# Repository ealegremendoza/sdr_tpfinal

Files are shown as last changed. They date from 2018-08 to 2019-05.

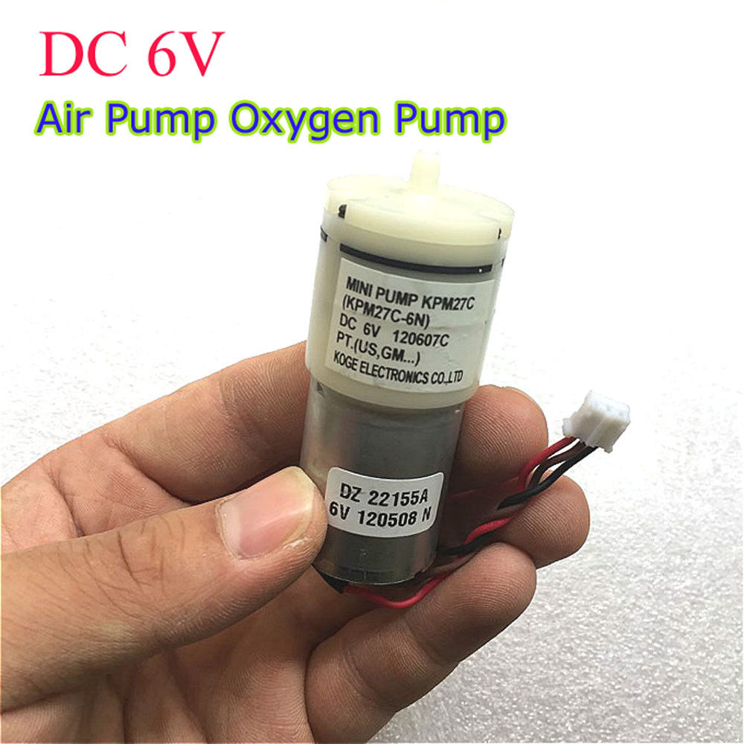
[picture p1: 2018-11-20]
docs/air_pump_1.jpg

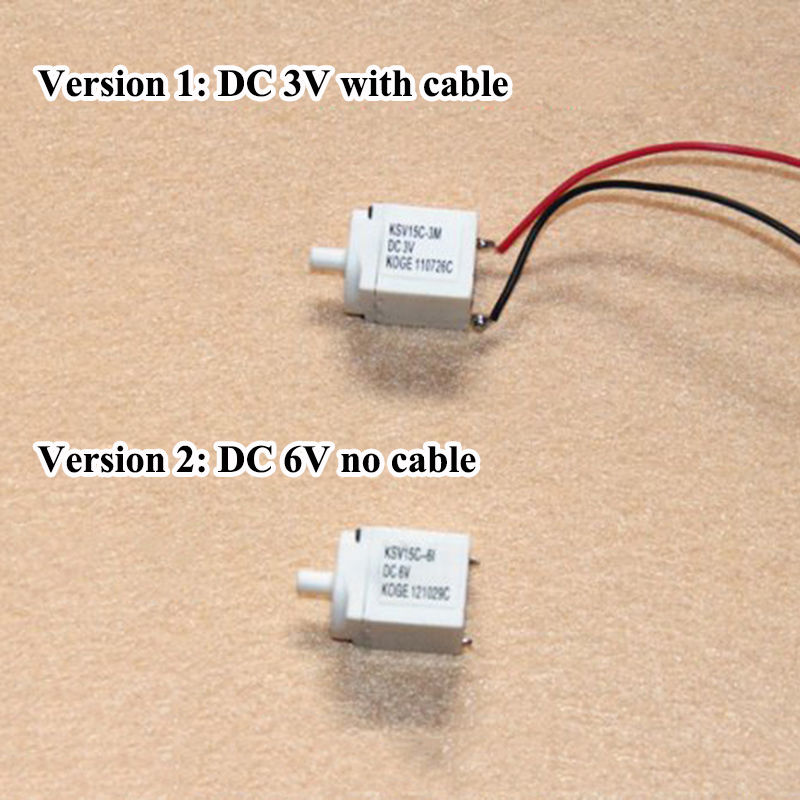
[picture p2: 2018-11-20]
docs/valve6.jpg

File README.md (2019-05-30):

# Proyecto Final de SDR 
## TENSIOMETRO DIGITAL

> TP Final de la materia Sistemas de Representación R1032 UTN FRBA. Ciclo lectivo 2018.

## Carpetas
>- *docs*: es encuentran archivos de interés para el proyecto.
>- *pcb*: desarrollo de la placa del proyecto.

---

Espero le sea de utilidad.

Ezequiel Alegre 

>Toda sugerencia será bienvenida.

>ealegremendoza@gmail.com

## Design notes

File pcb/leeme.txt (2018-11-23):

Guía de directorios y archivos más importantes:

/TensiometroDigital					-Contiene todo el trabajo práctico.
	
	PCB Layout Checklist.xslx			-Checklist

	/BOM						-Contiene la BOM del trabajo práctico. 
		TensiometroDigital_BOM_LINK_OCTOPART	-Contiene el link a la BOM en octopart.com
	
	/GABINETE
		GABINETE.fcstd1				-Contiene el gabinete creado en FREECAD.

	/GERBERS					-Contiene los archivos gerbers del PCB.

	/INFORME
		TensiometroDigita_informe.pdf		-Informe del trabajo práctico.

	/PANEL						-Contiene el panelizado del PCB.
		/panel-gerbers				-Contiene los archivos gerbers del panel.

	/PDFs
		TensiometroDigital-SCH_v1.pdf		-Esquemáticos del trabajo práctico.
		TensiometroDIgital-PCB_v1.pdf		-PCB del trabajo práctico.
		TD-gabinete-base-drawings_v1.pdf	-Drawings de la BASE del gabinete del trabajo práctico.
		TD-gabinete-tapa-drawings_v1.pdf	-Drawings de la TAPA del gabinete del trabajo práctico.

- El resto de los directorios y archivos no mencionados aquí son auxiliares para realizar el trabajo práctico.

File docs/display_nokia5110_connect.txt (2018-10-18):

https://www.algissalys.com/how-to/nokia-5110-lcd-on-raspberry-pi

Raspberry PI (physical pins)		5110 LCD

18	GPIO 24				RST (RESET)
24	SPI_CE0				CE (CHIP ENEABLE)
16 	GPIO 23				DC (DATA)
19	SPI_MOSI			DIN
23	SPI_SCLK			CLK
1	VCC 3.3V			VCC
11	GPIO 17				LIGHT
6	GND				GND

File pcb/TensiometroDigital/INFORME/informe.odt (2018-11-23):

# Descripción del proyecto diseñado

El siguiente proyecto es un medidor de presión arterial digital que utiliza un sensor de presión integrado, circuitos de acondicionamiento de señal analógica, un microcontrolador, una pantalla de cristal líquido y una memoria SD para el almacenamiento de datos.

El sistema de detección lee la presión del manguito (CP) y extrae los pulsos para el análisis y la determinación de la presión sistólica y diastólica. Este diseño utiliza un sensor de presión integrado de 50 kPa (Freescale Semiconductor, Inc. P / N: MPXV5050GP) que produce un rango de presión de 0 mm Hg a 300 mm Hg.

## Concepto del método oscilométrico

Este método es empleado por la mayoría de los dispositivos no invasivos automatizados. Una extremidad y su vasculatura están comprimidas por un manguito de compresión inflable y envolvente. La lectura de la presión arterial para los valores de presión arterial sistólica y diastólica se lee en el punto de identificación del parámetro.
El principio de medición simplificado del método oscilométrico es una medición de la amplitud del cambio de presión en el brazalete cuando el manguito se infla por encima de la presión sistólica. La amplitud aumenta repentinamente a medida que el pulso se rompe a través de la oclusión. Esto está muy cerca de la presión sistólica. A medida que la presión del manguito se reduce aún más, la pulsación aumenta en amplitud, alcanza un máximo y luego disminuye rápidamente. El índice de presión diastólica se toma donde comienza esta rápida transición. Por lo tanto, la presión arterial sistólica (PAS) y la presión arterial diastólica (DBP) se obtienen identificando la región donde hay un rápido aumento y luego disminuyen la amplitud de los pulsos, respectivamente. La presión arterial media (MAP) se encuentra en el punto de máxima oscilación.

## Descripción y funcionamiento del Hardware

La presión del manguito es detectada por el sensor de presión integrado de Freescale MPXV5005GP. La salida del sensor se divide en dos caminos para dos propósitos diferentes. Uno se usa como la presión del manguito, mientras que el otro se procesa más por un circuito.
Dado que el MPXV5050GP ve condicionada su señal por un amplificador operacional interno, la presión del brazalete puede interconectarse directamente con un convertidor analógico a digital (A / D) para la digitalización. La otra ruta filtrará y amplificará la señal de CP sin procesar para extraer una versión amplificada de las oscilaciones de CP, que son causadas por la expansión del brazo del sujeto cada vez que aumenta la presión en el brazo durante la sístole cardíaca.
La salida del sensor consta de dos señales; la señal de oscilación (≈ 1 Hz) que circula en la señal CP (≤ 0.04 Hz). Por lo tanto, un filtro de paso altos está diseñado para bloquear la señal CP antes de la amplificación de la señal de oscilación. Si la señal de CP no se atenúa adecuadamente, la línea de base de la oscilación no será constante y la amplitud de cada oscilación no tendrá la misma referencia para la comparación. La figura 1 muestra el amplificador de señal de oscilación junto con el filtro.

## Características

- Microcontrolador: LPC1769.
- Sensor de presión MPXV5050GP.
- Interfaz de usuario:
  - Display LCD de 48 x 84 puntos (ET-NOKIA LCD 5110, comunicación: SPI).
  - Teclas touch switch de START, SELECT y RESET.
  - Tecla switch de ON/OFF.
- Indicadores digitales:
  - Buzzer con habilitación vía jumper.
  - Led indicador.
- Memoria:
  - Conector a memoria SD (SD Oupiin 9004, comunicación: SPI).
  - Memoria 24LC256 (tipo de memoria: EEPROM, comunicación: I2C).
- Reloj de tiempo real (RTC) con batería de backup, CR2032.
- Autoreset por baja tensión.
- 8 pines para programación, SWD/JTAG interface.
- Alimentación mediante 2 baterías de Li-ion 18650, o 7V DC.
- Válvula KSV15C 6V DC.
- Bomba de aire KPM27C 6V DC.
- Manguera de conexión de medidor de presión digital.
- Dimensiones del gabinete (sin tener en cuenta el alto de las teclas):
  - Largo: 13 cm.
  - Ancho: 12 cm.
  - Alto: 6 cm.

# Diagramas Esquemáticos

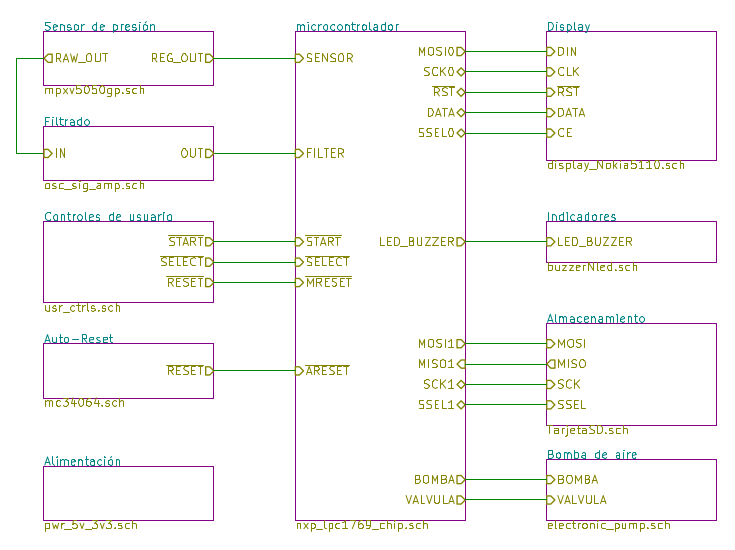
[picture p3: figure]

Figura 1. Diagrama esquemático, hoja 1.

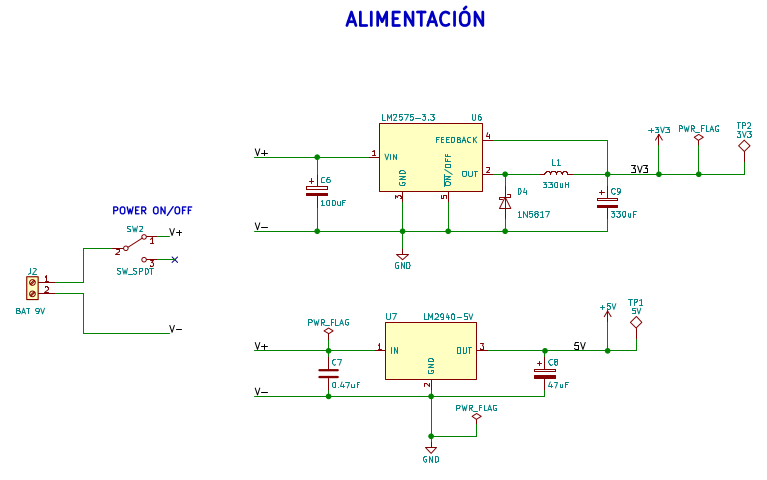
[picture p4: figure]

Figura 2. Diagrama esquemático, hoja 2.

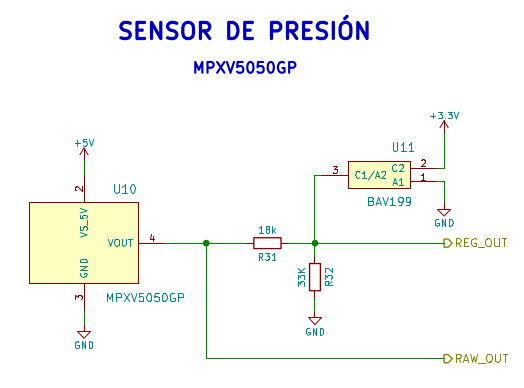
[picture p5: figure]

Figura 3. Diagrama esquemático, hoja 3.

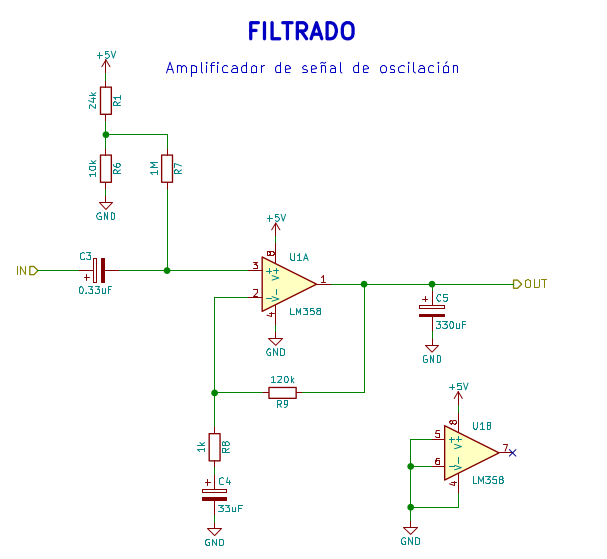
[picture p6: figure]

Figura 4. Diagrama esquemático, hoja 4.

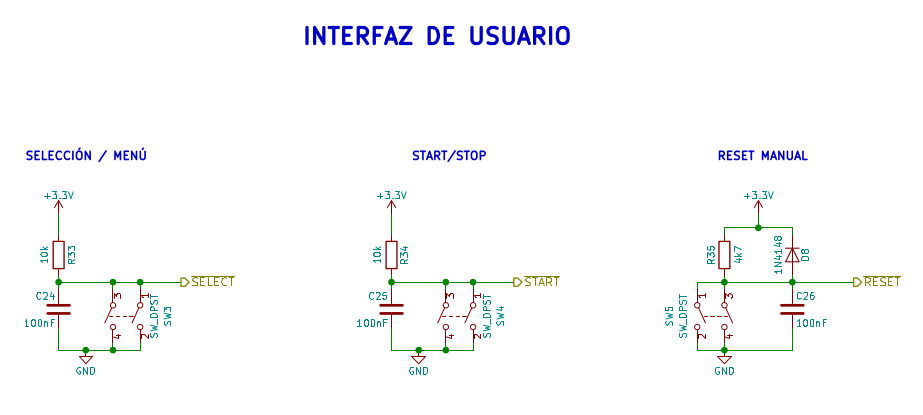
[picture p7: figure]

Figura 5. Diagrama esquemático, hoja 5.

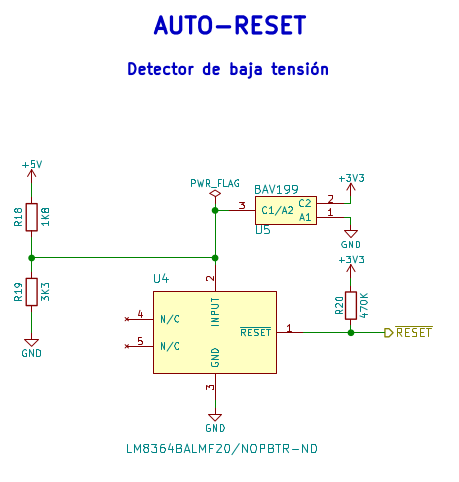
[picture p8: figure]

Figura 6. Diagrama esquemático, hoja 6.

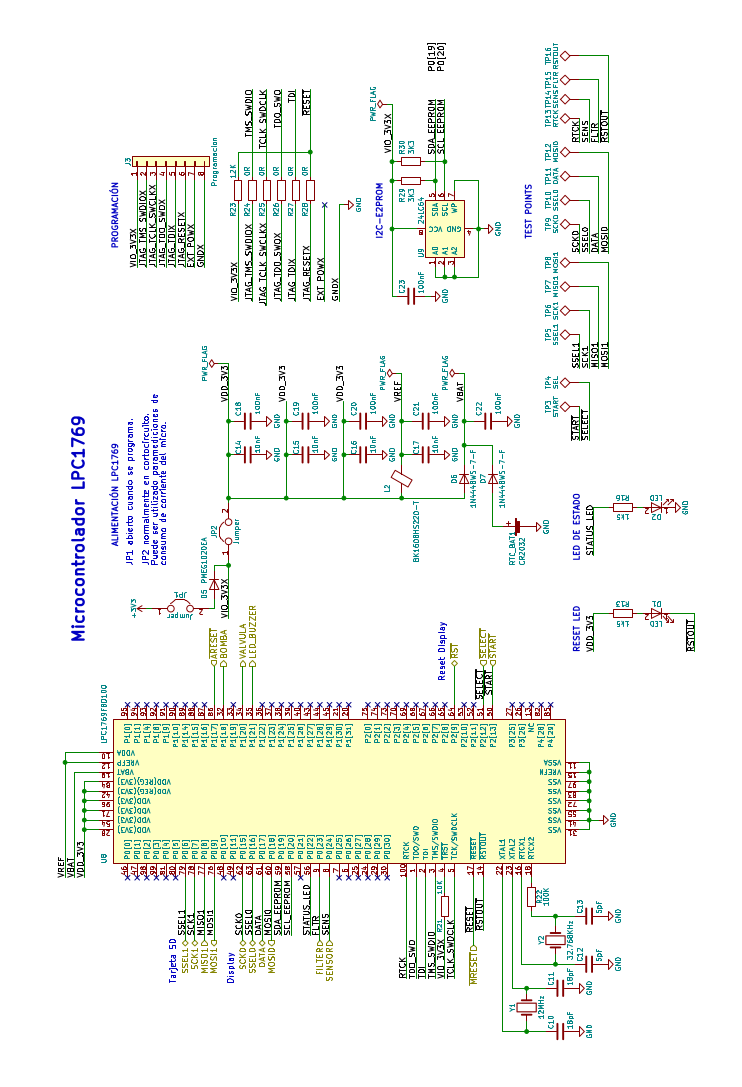
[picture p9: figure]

Figura 7. Diagrama esquemático, hoja 7.

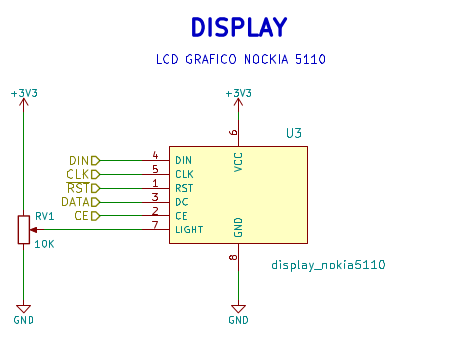
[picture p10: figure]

Figura 8. Diagrama esquemático, hoja 8.

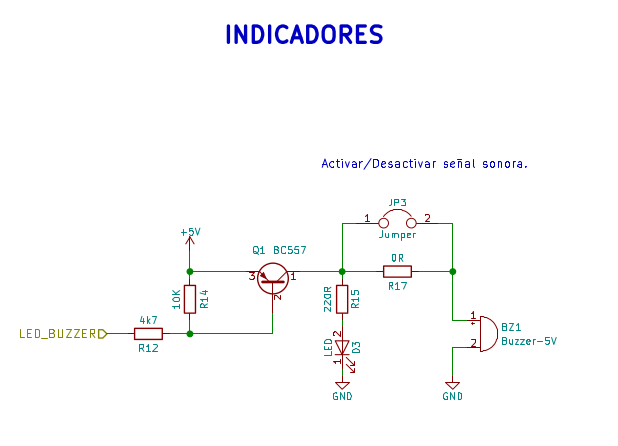
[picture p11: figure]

Figura 9. Diagrama esquemático, hoja 9.

Figura 10. Diagrama esquemático, hoja 10.

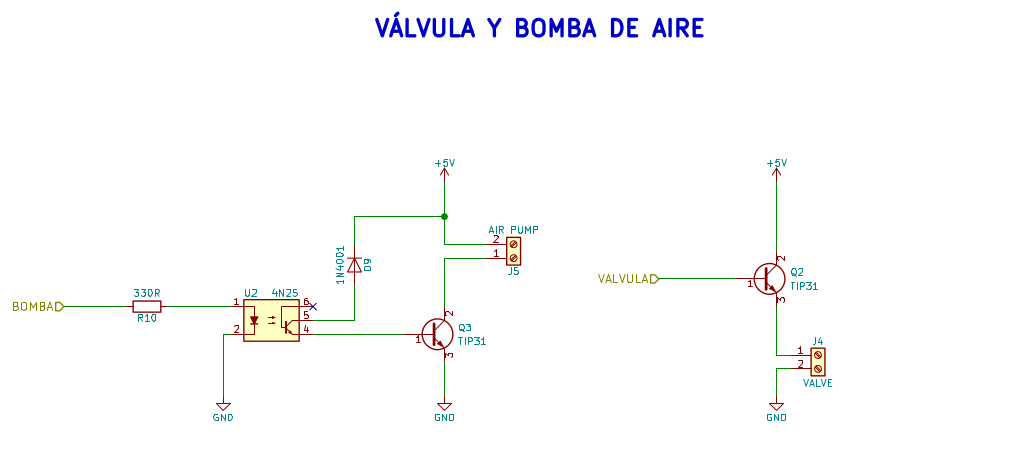
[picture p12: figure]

Figura 11. Diagrama esquemático, hoja 11.

# Lista de Componentes

# BOM

https://octopart.com/bom-tool/IMYVkySI

# PCB

## Placing

Figura 12. PCB, ubicación de componentes.

## Routing

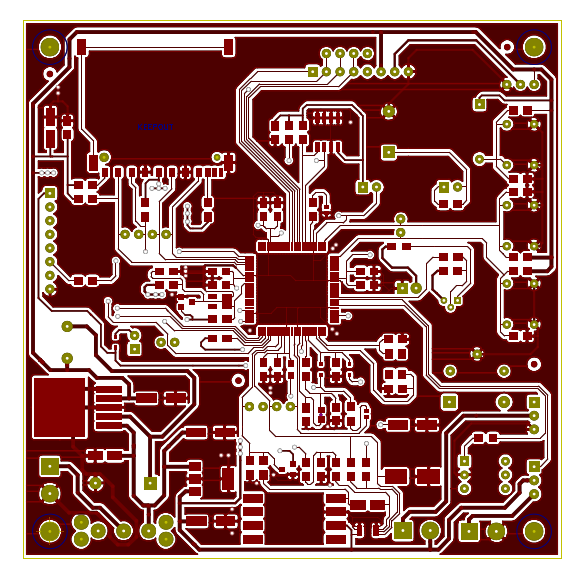
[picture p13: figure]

### Frente

Figura 13. PCB, ruteo frontal.

### Reverso

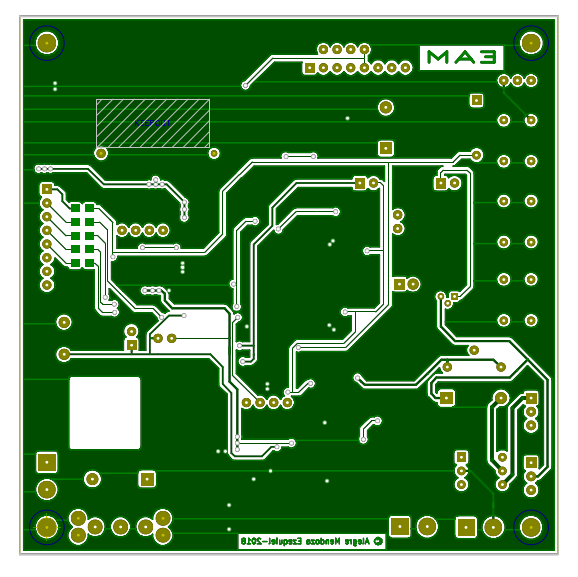
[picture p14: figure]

Figura 14. PCB, ruteo trasero.

### Vista general

Figura 14. PCB, vista general.

# Vistas 3D del PCB

## Vistas superior y posterior

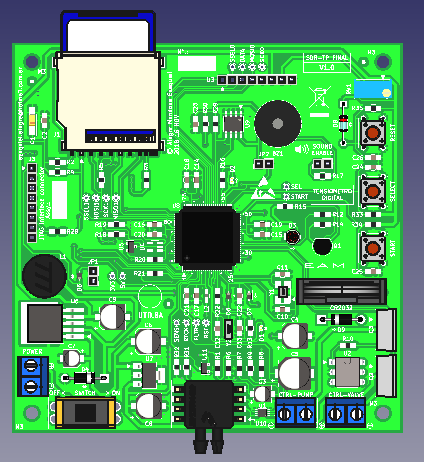
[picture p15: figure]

Figura 15. Vista 3D del PCB, vista superior.

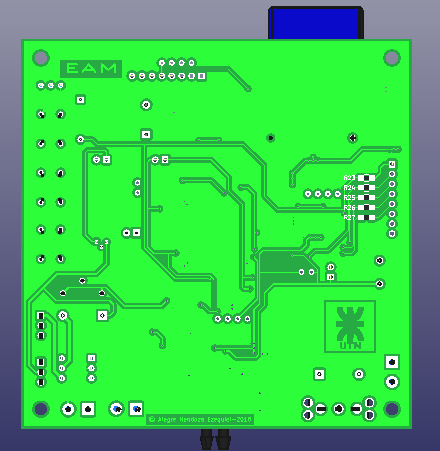
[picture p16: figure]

Figura 18. Vista 3D del PCB, vista posterior.

## Vista axonométrica

Figura 19. Vista 3D del PCB, vista axonométrica. (Con Display montado).

# Checklist

# Vistas 3D Gabinete

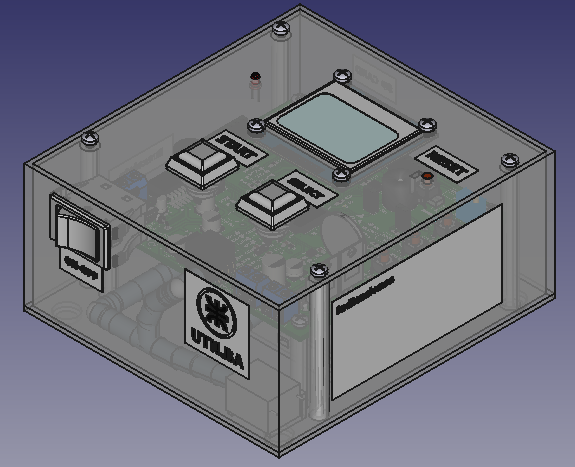
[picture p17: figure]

Figura 20. Vista 3D del Gabinete, vista axonométrica.

Figura 21. Vista 3D del Gabinete, vista superior.

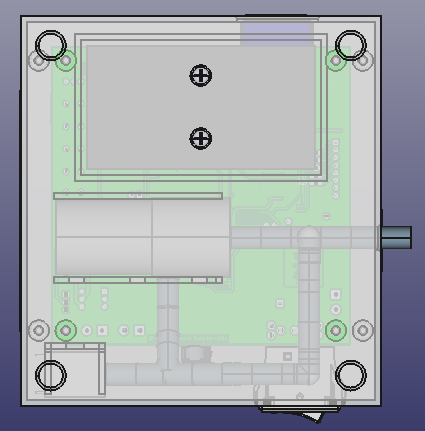
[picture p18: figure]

Figura 22. Vista 3D del Gabinete, vista inferior.

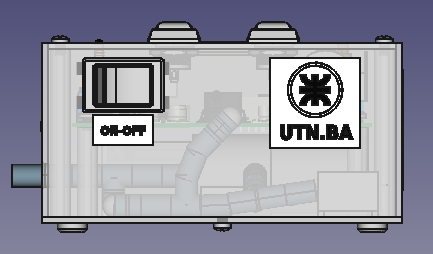
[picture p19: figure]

Figura 23. Vista 3D del Gabinete, frente.

Figura 24. Vista 3D del Gabinete, derecha.

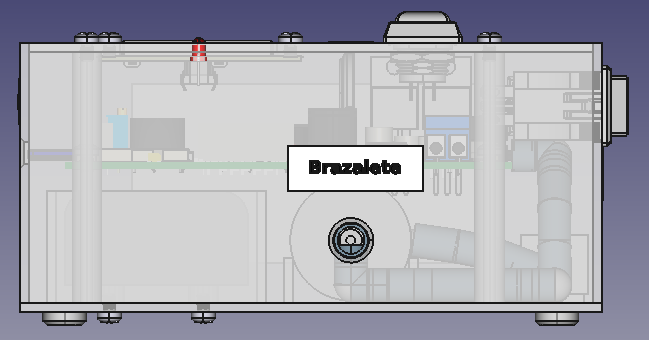
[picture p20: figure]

Figura 25. Vista 3D del Gabinete, izquierda.

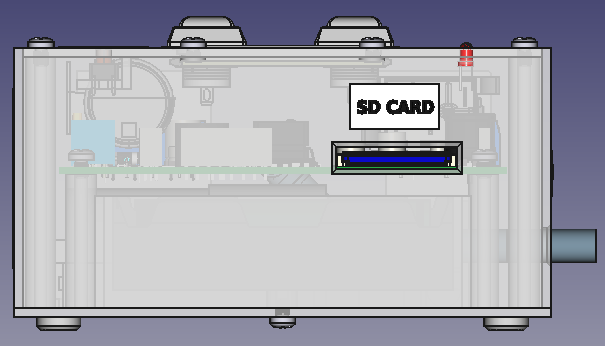
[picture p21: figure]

Figura 26. Vista 3D del Gabinete, vista posterior.

## Drawings - Base

Figura 27. Drawings Gabinete, parte 1.

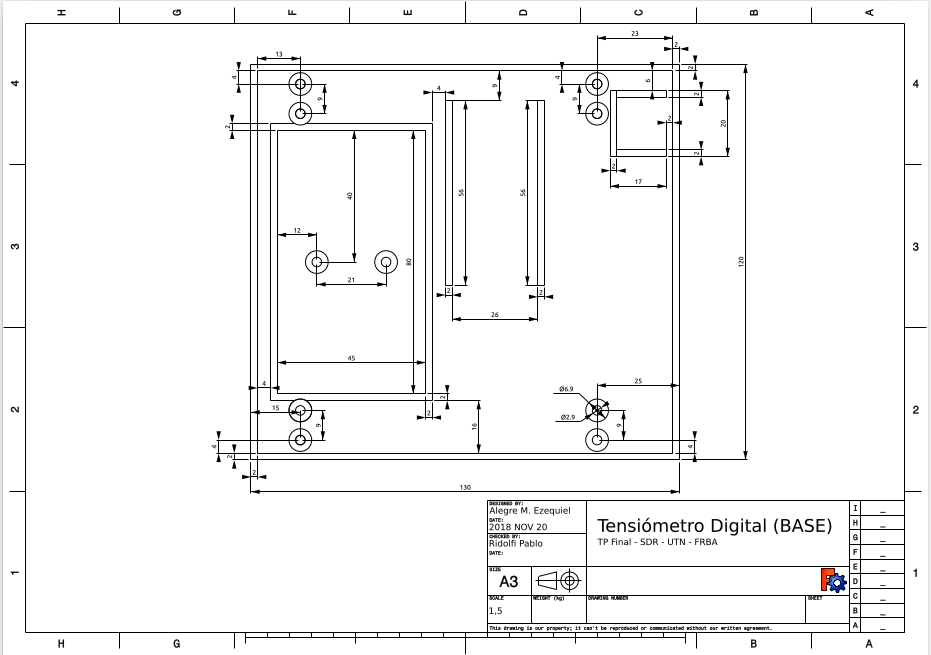
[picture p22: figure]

Figura 28. Drawings Gabinete, parte 2.

Figura 29. Drawings Gabinete, parte 3.

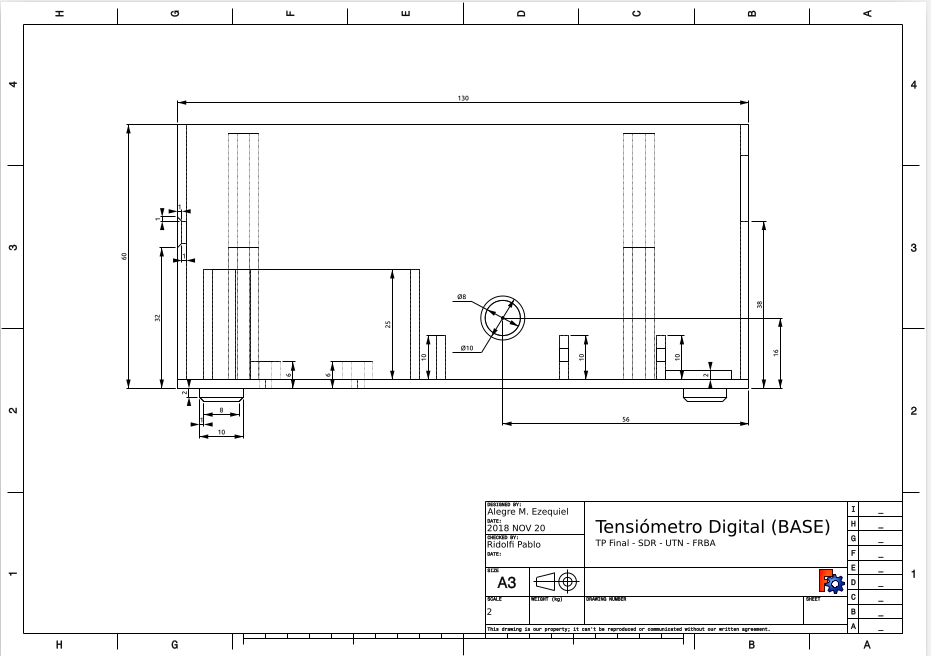
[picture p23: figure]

Figura 30. Drawings Gabinete, parte 4.

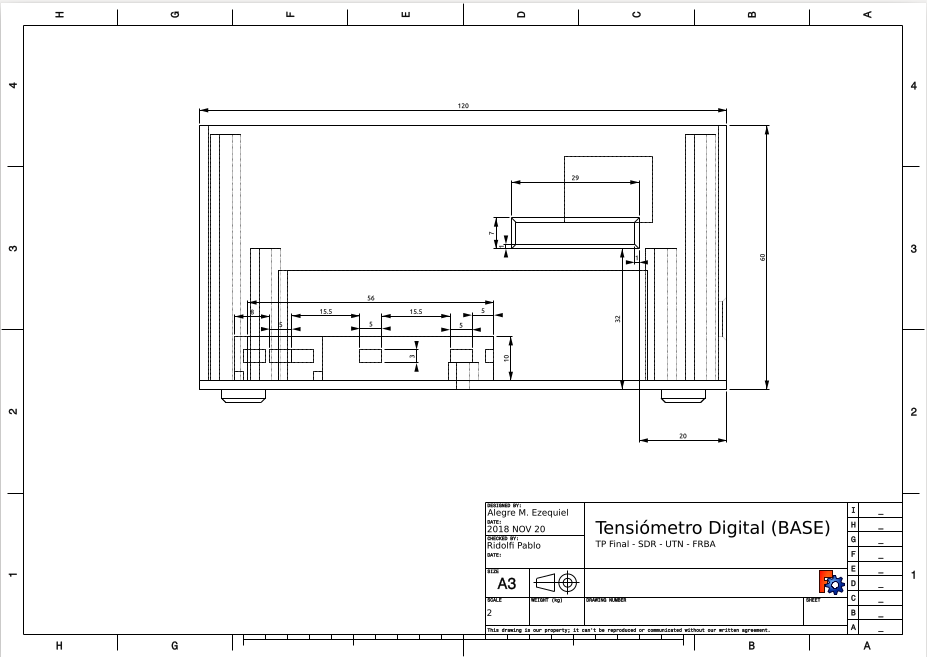
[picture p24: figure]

Figura 31. Drawings Gabinete, parte 5.

Figura 32. Drawings Gabinete, parte 6.

## Drawings - Tapa

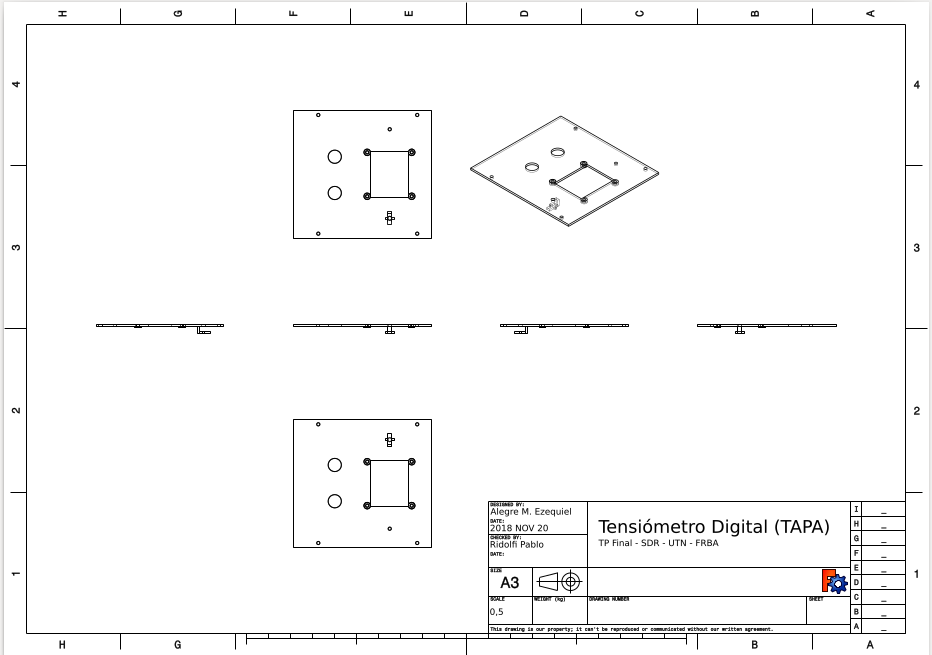
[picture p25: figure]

Figura 33. Drawings Gabinete, parte 7.

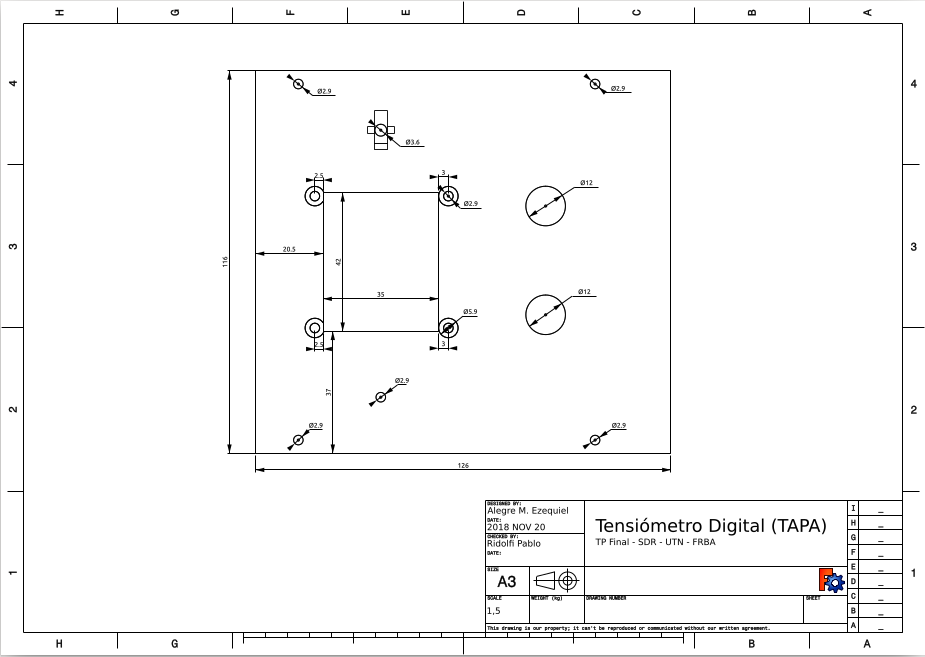
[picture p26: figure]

Figura 34. Drawings Gabinete, parte 8.

Figura 35. Drawings Gabinete, parte 9.

# Descripción Test-Points

# Descripción de conectores

# Configuración y función de los jumpers

- JP1: Abierto cuando se programa.
- JP2: Normalmente cortocircuitado. Puede ser utilizado para mediciones de consumo de corriente del microcontrolador.
- JP3: Activa la señal sonora cuando está cortocircuitado. Puede conectarse en su lugar un pulsador con retención para facilitarle al usuario controlar esto. Por defecto está cortocircuitado por R17. Remover el resistor para utilizar el jumper.

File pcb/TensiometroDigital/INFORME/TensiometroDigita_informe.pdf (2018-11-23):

## SISTEMAS DE REPRESENTACIÓN


Alumno: Alegre Mendoza Ezequiel.

Legajo: 153204-2 | CURSO: R1032

Docente: Ridolfi Pablo.
Auxiliar Docente: Delconte Franco. Asiste los días: Jueves.
En el turno: Tarde.

### TRABAJO PRÁCTICO FINAL TENSIÓMETRO DIGITAL

## ÍNDICE

Descripción del proyecto diseñado

El siguiente proyecto es un medidor de presión arterial digital que utiliza un sensor de presión integrado, circuitos de acondicionamiento de señal analógica, un microcontrolador, una pantalla de cristal líquido y una memoria SD para el almacenamiento de datos.
El sistema de detección lee la presión del manguito (CP) y extrae los pulsos para el análisis y la determinación de la presión sistólica y diastólica. Este diseño utiliza un sensor de presión integrado de 50 kPa (Freescale Semiconductor, Inc. P / N: MPXV5050GP) que produce un rango de presión de 0 mm Hg a 300 mm Hg.

Concepto del método oscilométrico
Este método es empleado por la mayoría de los dispositivos no invasivos automatizados. Una extremidad y su vasculatura están comprimidas por un manguito de compresión inflable y envolvente. La lectura de la presión arterial para los valores de presión arterial sistólica y diastólica se lee en el punto de identificación del parámetro.
El principio de medición simplificado del método oscilométrico es una medición de la amplitud del cambio de presión en el brazalete cuando el manguito se infla por encima de la presión sistólica. La amplitud aumenta repentinamente a medida que el pulso se rompe a través de la oclusión. Esto está muy cerca de la presión sistólica. A medida que la presión del manguito se reduce aún más, la pulsación aumenta en amplitud, alcanza un máximo y luego disminuye rápidamente. El índice de presión diastólica se toma donde comienza esta rápida transición. Por lo tanto, la presión arterial sistólica (PAS) y la presión arterial diastólica (DBP) se obtienen identificando la región donde hay un rápido aumento y luego disminuyen la amplitud de los pulsos, respectivamente. La presión arterial media (MAP) se encuentra en el punto de máxima oscilación.

Descripción y funcionamiento del Hardware
La presión del manguito es detectada por el sensor de presión integrado de Freescale MPXV5005GP. La salida del sensor se divide en dos caminos para dos propósitos diferentes. Uno se usa como la presión del manguito, mientras que el otro se procesa más por un circuito.
Dado que el MPXV5050GP ve condicionada su señal por un amplificador operacional interno, la presión del brazalete puede interconectarse directamente con un convertidor analógico a digital (A /
D) para la digitalización. La otra ruta filtrará y amplificará la señal de CP sin procesar para extraer una versión amplificada de las oscilaciones de CP, que son causadas por la expansión del brazo del sujeto cada vez que aumenta la presión en el brazo durante la sístole cardíaca.
La salida del sensor consta de dos señales; la señal de oscilación (≈ 1 Hz) que circula en la señal CP (≤ 0.04 Hz). Por lo tanto, un filtro de paso altos está diseñado para bloquear la señal CP antes de la amplificación de la señal de oscilación. Si la señal de CP no se atenúa adecuadamente, la línea de base de la oscilación no será constante y la amplitud de cada oscilación no tendrá la misma referencia para la comparación. La figura 1 muestra el amplificador de señal de oscilación junto con el filtro.

Características
- Microcontrolador: LPC1769.
- Sensor de presión MPXV5050GP.
- Interfaz de usuario:
- Display LCD de 48 x 84 puntos (ET-NOKIA LCD 5110, comunicación: SPI).
- Teclas touch switch de START, SELECT y RESET.
- Tecla switch de ON/OFF.
- Indicadores digitales:
- Buzzer con habilitación vía jumper.
- Led indicador.
- Memoria:
- Conector a memoria SD (SD Oupiin 9004, comunicación: SPI).
- Memoria 24LC256 (tipo de memoria: EEPROM, comunicación: I2C).
- Reloj de tiempo real (RTC) con batería de backup, CR2032.
- Autoreset por baja tensión.
- 8 pines para programación, SWD/JTAG interface.
- Alimentación mediante 2 baterías de Li-ion 18650, o 7V DC.
- Válvula KSV15C 6V DC.
- Bomba de aire KPM27C 6V DC.
- Manguera de conexión de medidor de presión digital.
- Dimensiones del gabinete (sin tener en cuenta el alto de las teclas):
- Largo: 13 cm.
- Ancho: 12 cm.
- Alto: 6 cm.


Diagramas Esquemáticos

Figura 1. Diagrama esquemático, hoja 1.

Figura 2. Diagrama esquemático, hoja 2.


Figura 3. Diagrama esquemático, hoja 3.

Figura 4. Diagrama esquemático, hoja 4.


Figura 5. Diagrama esquemático, hoja 5.

Figura 6. Diagrama esquemático, hoja 6.


Figura 7. Diagrama esquemático, hoja 7.


Figura 8. Diagrama esquemático, hoja 8.

Figura 9. Diagrama esquemático, hoja 9.


Figura 10. Diagrama esquemático, hoja 10.

Figura 11. Diagrama esquemático, hoja 11.

Lista de Componentes

BOM
https://octopart.com/bom-tool/IMYVkySI
REFERENCIA | VALOR | Cant. | REFERENCIA | VALOR | Cant.
BZ1 | Buzzer-5V | 1 | R22 | 100K | 1
C1 | 1uF x 16V | 1 | R23 | 12K | 1
C10,C11 | 18pF | 2 | R31 | 18k | 1
C12,C13 | 5pF | 2 | R4,R5,R32 | 33K | 3
C2 | 100n | 1 | R6,R33,R34 | 10k | 3
C3 | 0.33uF | 1 | R7 | 1M | 1
C4 | 33uF | 1 | R8 | 1k | 1
C5 | 330uF | 1 | R9 | 120k | 1
C6 | 100uF | 1 | RTC_BAT1 | CR2032 | 1
C7 | 0.47uF | 1 | RV1 | 10K | 1
C8 | 47uF | 1 | SW2 | SW_SPDT | 1
C9 | 330uF | 1 | SW3-SW5 | SW_DPST | 3
C14-C17 | 10nF | 4 | TP1 | 5V | 1
C18-C26 | 100nF | 9 | TP10 | SSEL0 | 1
D1,D2 | LED | 2 | TP11 | DATA | 1
D3 | LED | 1 | TP12 | MOSI0 | 1
D4 | 1N5817 | 1 | TP13 | RTCK | 1
D5 | PMEG1020EA | 1 | TP14 | SENS | 1
D6,D7 | 1N4448WS-7-F | 2 | TP15 | FLTR | 1
D8 | 1N4148 | 1 | TP16 | RSTOUT | 1
D9 | 1N4001 | 1 | TP2 | 3V3 | 1
J1 | SD_Card | 1 | TP3 | START | 1
J2 | BAT 9V | 1 | TP4 | SEL | 1
J3 | Programacion | 1 | TP5 | SSEL1 | 1
J4 | VALVE | 1 | TP6 | SCK1 | 1
J5 | AIR PUMP | 1 | TP7 | MISO1 | 1
JP1-JP3 | Jumper | 3 | TP8 | MOSI1 | 1
L1 | 330uH | 1 | TP9 | SCK0 | 1
L2 | BK1608HS220-T | 1 | U1 | LM358 | 1
Q1 | BC557 | 1 | U10 | MPXV5050GP | 1
Q2,Q3 | TIP31 | 2 | U2 | 4N25 | 1
R1 | 24k | 1 | U3 | display_nokia5110 | 1
R10 | 330R | 1 | U4 | LM8364BALMF20/NOPBTR-ND | 1
R12,R35 | 4k7 | 2 | U5,U11 | BAV199 | 2
R13,R16 | 1k5 | 2 | U6 | LM2575-3.3 | 1
R15 | 220R | 1 | U7 | LM2940-5V | 1
R17,R24-R28 | 0R | 6 | U8 | LPC1769FBD100 | 1
R18 | 1K8 | 1 | U9 | 24LC64 | 1
R19,R29,R30 | 3K3 | 3 | Y1 | 12MHz | 1
R2,R3,R14,R21 | 10K | 4 | Y2 | 32.768KHz | 1
R20 | 470K | 1

PCB

Placing


Figura 12. PCB, ubicación de componentes.


Routing

Frente

Figura 13. PCB, ruteo frontal. Reverso

Figura 14. PCB, ruteo trasero.

Vista general


Figura 14. PCB, vista general.

Vistas 3D del PCB

Vistas superior y posterior


Figura 15. Vista 3D del PCB, vista superior.


Figura 18. Vista 3D del PCB, vista posterior.

Vista axonométrica


Figura 19. Vista 3D del PCB, vista axonométrica. (Con Display montado).

Checklist

Ubicación de componentes | Comentarios | Condición
1. Orientación consistente de componentes SMD | | .CUMPLE
2. Espacio para herramientas de retrabajo | | .CUMPLE
3. Verificar componentes polarizados | | .CUMPLE
4. Utilizar grilla de 50 mil para componentes THT | 20 mil para todo el placing | .NO CUMPLE
5. Verificar orientación de todos los conectores | | .CUMPLE
6. Verificar espacio mínimo entre cuerpo de componentes | | .CUMPLE
7. Capacitores de desacople (bypass) cerca de pines de alimentación de los IC | | .CUMPLE
8. Verificar terminadores en serie cercanos a la fuente | | NO APLICA
9. Drivers I/O cercanos a donde las señales abandonan el PCB | | .CUMPLE
10. Torretas a GND, pistas de alimentación y test points, todos etiquetados. | | .CUMPLE
11. Filtros EMI y RFI lo más cerca posible a puntos de entrada y salida en áreas blindadas. | | NO APLICA
12. Ubicar componentes de manera tal que un rework o reparación de un componente no requiera remover otros. | | .CUMPLE
13. Los potenciómetros deberían incrementar la cantidad controlada en sentido de las agujas del reloj. | | .CUMPLE
14. Verificar si los orificios de montaje deben estar aislados eléctricamente o no. | | .CUMPLE
15. Verificar distancia de seguridad de los orificios de montaje hacia otros componentes. | | .CUMPLE
16. Verificar factor de forma de los pads SMD. | | .CUMPLE
17. Fiduciales para ensamle automático. | | .CUMPLE
18. Distancia de seguridad suficiente para ICs con zócalo. | | .CUMPLE
Ruteo/pistas | Comentarios | Condición
1. Comunes digitales y analógicos unidos en un solo punto. | | .CUMPLE
2. Verificar pistas debajo de componentes ruidosos o sensibles. | | .CUMPLE
3. No ubicar vias debajo de resistores de metalfilm u otros componentes con aislación pobre. | | .CUMPLE
4. Verificar pistas susceptibles a puentes de soldadura. | | .CUMPLE
5. Verificar pistas sin conexión en un extremo, a menos que sea a propósito. | | .CUMPLE
6. Asegurar que el CAD unifica o no señales Vcc/Vdd y Vss/GND según lo requiera el diseño. | | .CUMPLE
7. Utilizar múltiples vías en pistas de alta corriente y/o baja impedancia. | | .CUMPLE
8. Observar keepout de componentes y pistas. | | .CUMPLE
9. Utilizar planos de GND donde sea posible. | | .CUMPLE
Dimensiones | Comentarios | Condición
1. Diámetro de orificios debe considerar el metalizado. | | .CUMPLE
2. Diámetro de orificios más grande que el diámetro de pata al menos en 10 mils. | | .CUMPLE
3. Ancho de texto en silkscreen 0.25mm o más. | | .CUMPLE
4. Pad al menos 0.4mm más grande que drill. | | .CUMPLE
5. Componentes ubicados al menos a 5mm del borde del PCB. | | .CUMPLE
6. Test pads ubicados al menos a 5mm del borde del PCB. | | .CUMPLE
7. Pistas al menos a 0.5mm del borde del PCB. | | .CUMPLE
8. Tolerancia de drills especificada. | Valor por defecto de KICAD | .CUMPLE
9. Tolerancia de máscara antisoldante especificada. | Valor por defecto de KICAD | .CUMPLE
10. Tolerancia de pistas especificada. | Valor por defecto de KICAD | .CUMPLE
11. Tolerancia de serigrafía especificada. | Valor por defecto de KICAD | .CUMPLE
12. Ancho de pista suficiente para la corriente conducida. | | .CUMPLE
13. Distancia suficiente entre pistas de alto voltaje. | | NO APLICA
Serigrafía (silkscreen) | Comentarios | Condición
1. Evitar serigrafía sobre vías sin máscara u orificios. | | .CUMPLE
2. Todos los textos y leyendas legibles en una o dos direcciones. | | .CUMPLE
3. Logo de la compañía en serigrafía. | | .CUMPLE
4. Logo de la compañía en cobre. | | .CUMPLE
5. Nota de copyright en PCB. | | .CUMPLE
6. Fecha en PCB. | | .CUMPLE
7. Número de parte en PCB. | | .CUMPLE
8. Número de parte de montaje en PCB. | | .CUMPLE
9. Revisión del PCB en serigrafía. | | .CUMPLE
10. Espacio para revisión de montaje en serigrafía. | | .CUMPLE
11. Espacio para número de serie en serigrafía. | | .CUMPLE
12. Ubicar todo el texto de la serigrafía de manera tal que sea legible cuando los componentes están montados. | | .CUMPLE
13. Todos los ICs deben tener el pin 1 debidamente marcado y visible con el IC instalado. | | .CUMPLE
14. ICs de muchos pines deberían tener los pines extremos numerados para facilitar su identificación. | | .CUMPLE
15. Marcas cada 5 o 10 pines en ICs o conectores de muchos pines para facilitar su identificación. | | .CUMPLE
Otros | Comentarios | Condición
1. Utilizar DRC y ERC habilitados en el CAD. | | .CUMPLE
2. Tomar las precauciones necesarias en circuitos de alta frecuencia. | | NO APLICA
3. Colocar conectores y pines extra en prototipos para pruebas, por si es necesario. | | .CUMPLE
4. Verificar dimensiones y formas de orificios en conectores raros (rectangulares, ovalados). | | .CUMPLE
5. Verificar si la máscara antisoldante cubre o no cubre las vías. | Por defecto de KICAD | .CUMPLE
6. No rutear ángulos agudos. | | .CUMPLE
7. Verificar profundidad de la máscara antisoldante. | | NO APLICA
8. Verificar el netlist manualmente o por inspección visual. | | .CUMPLE
9. Verificar si existen conexiones de un único pin y si son intencionales. | | .CUMPLE
10. Verificar si el origen de orificios es un pad de referencia. | | .CUMPLE
11. Anotar en layer auxiliar ancho del PCB, material y peso del cobre. | | .CUMPLE
12. Utilizar aislamiento térmico (thermal relief) en capas internas de distribución de alimentación. | | NO APLICA
13. Verificar que las aperturas para pasta de estaño sean del tamaño adecuado. | | .CUMPLE
14. Verificar si se permiten blind/buried vias en PCB multicapa. | | NO APLICA
15. Definir correctamente el panelizado del PCB. | | .CUMPLE
16. Encapsulados metálicos de cristales de alta frecuencia deberían conectarse a GND. | | .CUMPLE

## Vistas 3D Gabinete


Figura 20. Vista 3D del Gabinete, vista axonométrica.

Figura 21. Vista 3D del Gabinete, vista superior.


Figura 22. Vista 3D del Gabinete, vista inferior.

Figura 23. Vista 3D del Gabinete, frente.


Figura 24. Vista 3D del Gabinete, derecha.

Figura 25. Vista 3D del Gabinete, izquierda.

Figura 26. Vista 3D del Gabinete, vista posterior.


Drawings - Base

Figura 27. Drawings Gabinete, parte 1.

Figura 28. Drawings Gabinete, parte 2.


Figura 29. Drawings Gabinete, parte 3.

Figura 30. Drawings Gabinete, parte 4.


Figura 31. Drawings Gabinete, parte 5.

Figura 32. Drawings Gabinete, parte 6.


Drawings - Tapa

Figura 33. Drawings Gabinete, parte 7.

Figura 34. Drawings Gabinete, parte 8.


Figura 35. Drawings Gabinete, parte 9.

Descripción Test-Points

Descripción de conectores

Configuración y función de los jumpers
- JP1: Abierto cuando se programa.
- JP2: Normalmente cortocircuitado. Puede ser utilizado para mediciones de consumo de corriente del microcontrolador.
- JP3: Activa la señal sonora cuando está cortocircuitado. Puede conectarse en su lugar un pulsador con retención para facilitarle al usuario controlar esto. Por defecto está cortocircuitado por R17. Remover el resistor para utilizar el jumper.
TestPoint | Descripción
TP1 | Salida del regulador de 5V DC.
TP2 | Salida del regulador de 3,3V DC.
TP3 | START
TP4 | SELECT
TP5 | SD: SSEL1
TP6 | SD: SCK1
TP7 | SD: MISO1
TP8 | SD: MOSI1
TP9 | Display: SCK0
TP10 | Display: SSEL0
TP11 | Display: DATA
TP12 | Display: MOSI0
TP13 | RTCK
TP14 | Salida del sensor, señal CP.
TP15 | Salida del Filtro, Oscilación amplificada.
TP16 | Reset Out
Conector | Descripción
POWER | Entrada de alimentación. 6-7V DC.
CTRL-PUMP | Control de la bomba de aire de 6V DC.
CTRL-VALVE | Control de la válvula de 6V DC.
ON-OFF (SW2) Llave de encendido/apagado. SELECT (SW3) Botón de selección.
START(SW4) | Botón de start.
RESET(SW5) | Botón de reset manual.
DISPLAY(U3) | Conexión a display LCD 5110.
SD (J1) | Conector para tarjeta SD.
JTAG (J3) | Conector para programación, JTAG.

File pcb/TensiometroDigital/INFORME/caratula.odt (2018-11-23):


SISTEMAS DE REPRESENTACIÓN

Alumno: Alegre Mendoza Ezequiel.

Legajo: 153204-2 | CURSO: R1032

Docente: Ridolfi Pablo.

Auxiliar Docente: Delconte Franco.

Asiste los días: Jueves.

En el turno: Tarde.

TRABAJO PRÁCTICO FINAL

TENSIÓMETRO DIGITAL


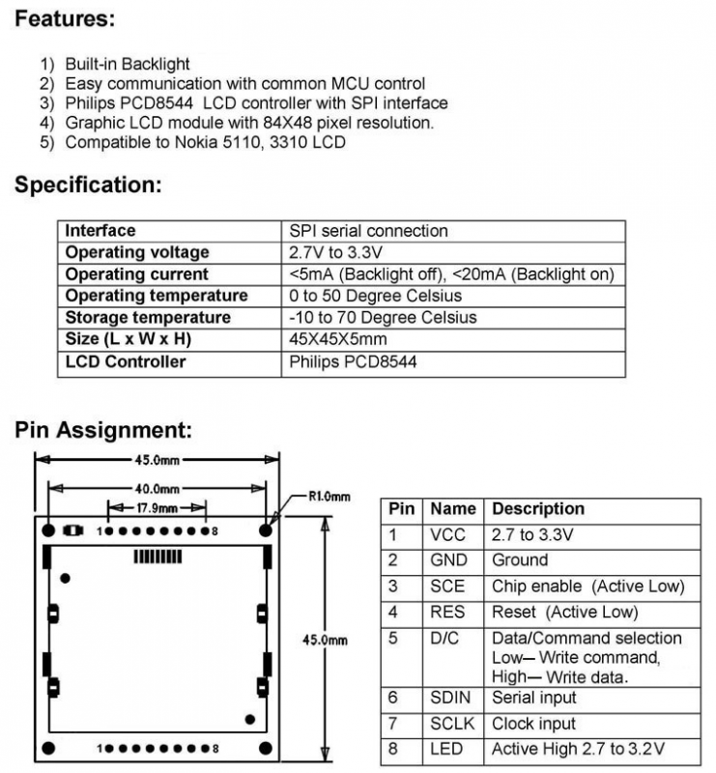
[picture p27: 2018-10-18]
docs/L0048P001314832511.png

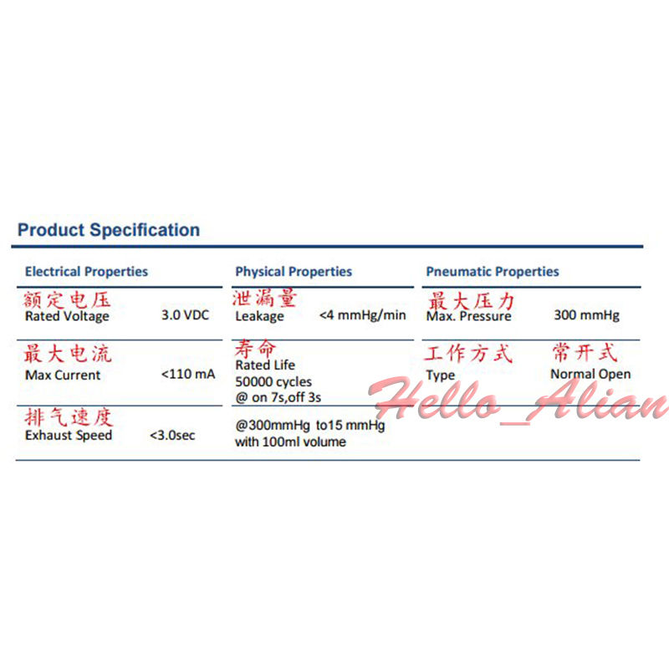
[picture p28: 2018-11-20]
docs/valve5.jpg

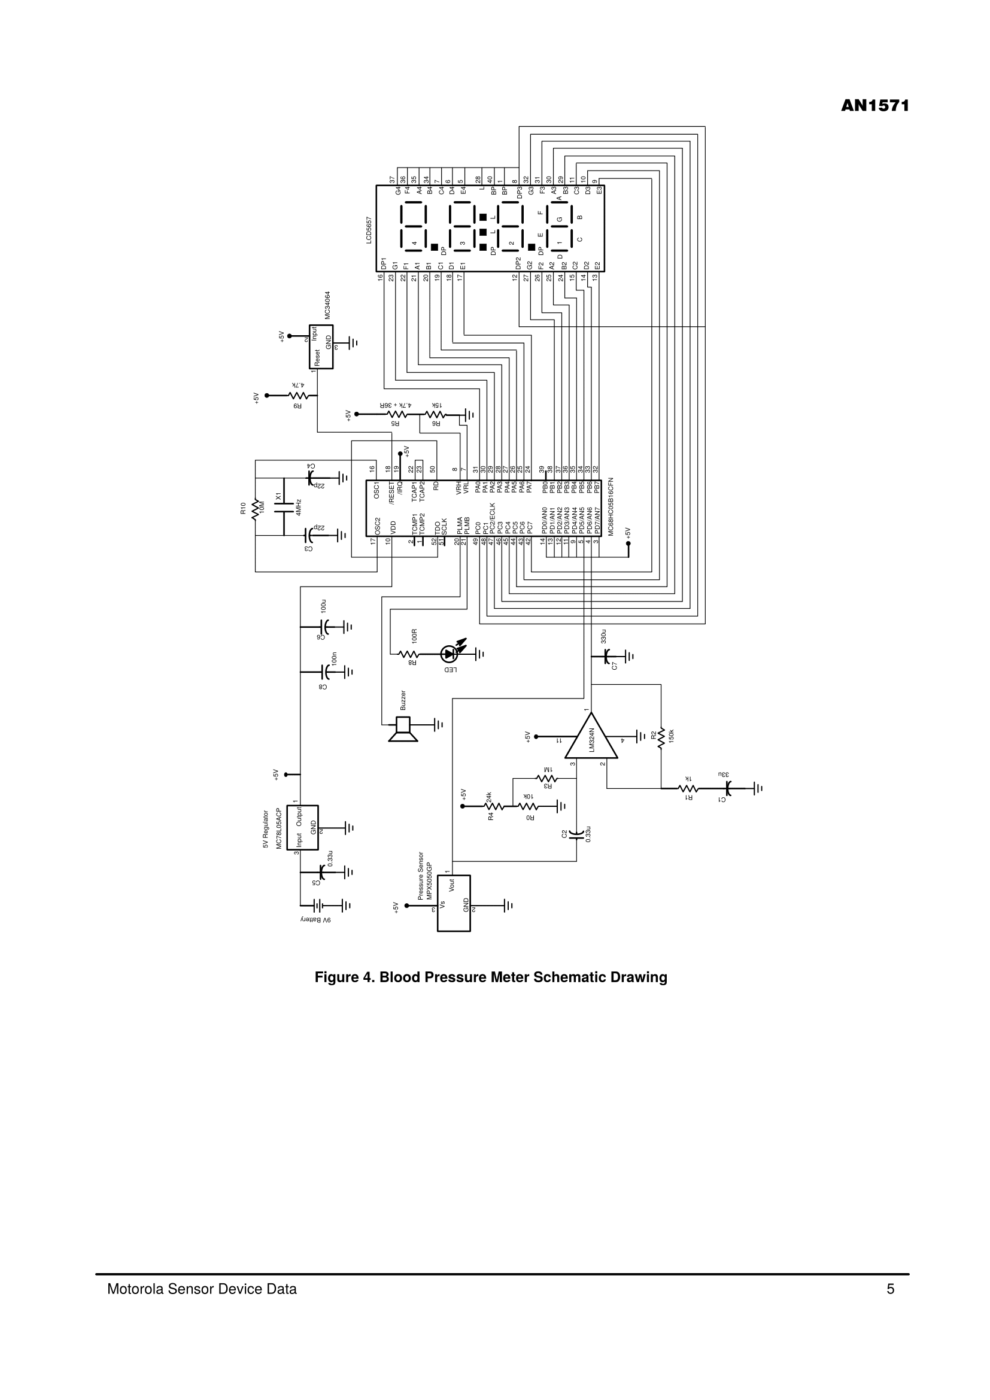
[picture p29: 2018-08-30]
docs/circuitoTensiometroDigital-1.png

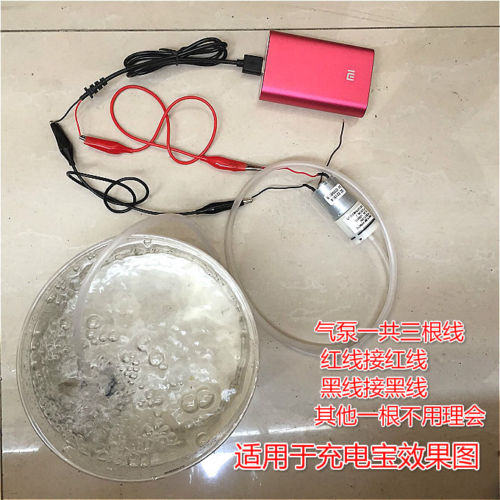
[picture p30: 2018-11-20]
docs/air_pump_4.jpg

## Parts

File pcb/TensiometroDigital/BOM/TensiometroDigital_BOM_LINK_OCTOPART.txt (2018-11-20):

BOM OCTOPART
https://octopart.com/bom-tool/IMYVkySI

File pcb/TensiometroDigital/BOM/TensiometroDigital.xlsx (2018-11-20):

 |  |  | 1
Refs | Manf# | Qty
BZ1 | CMI-1275C-050 | 1
C1 | TMCP1C105MTRF | 1
C10,C11 | CBR08C180FAGAC | 2
C12,C13 | 08053A5R0CAT2A | 2
C2 | C0805X104J5RACAUTO | 1
C3 | 865230640003 | 1
C4 | UCQ1E330MCL1GB | 1
C5 | 865080253011 | 1
C6 | UCQ1A101MCL1GS | 1
C7 | 865250640004 | 1
C8 | UCQ1C470MCL1GB | 1
C9 | 865090145008 | 1
C14-C17 | C0805C103JARACTU | 4
C18-C26 | C0805X104J5RACAUTO | 9
D1,D2 | SML-P11VTT86R | 2
D3 | HLMP-K101 | 1
D4 | 1N5817 | 1
D5 | PMEG1020EA | 1
D6,D7 | 1N4448WS-7-F | 2
D8 | 1N4148 | 1
D9 | 1N4001-T | 1
J1 | 2041021-3 | 1
J2 | 1776493-2 | 1
J3 |  | 1
J4 | 1776493-2 | 1
J5 | 1776493-2 | 1
JP1-JP3 |  | 3
L1 | RFC1010B-334KE | 1
L2 | BK1608HS220-T | 1
Q1 | BC557 | 1
Q2,Q3 | TIP31 | 2
R1 | RC0805DR-0724KL | 1
R10 | SG73G2ATTD3300D | 1
R12,R35 | SG73G2ATTD4701D | 2
R13,R16 | SG73G2ATTD1501D | 2
R15 | SG73G2ATTD2200D | 1
R17,R24-R28 | AC0805FR-070RL | 6
R18 | RT0805DRD071K8L | 1
R19,R29,R30 | SG73G2ATTD3301D | 3
R2,R3,R14,R21 | SG73G2ATTD1002D | 4
R20 | KTR10EZPF4703 | 1
R22 | SG73G2ATTD1003D | 1
R23 | RT0805DRD0712KL | 1
R31 | RT0805DRD0718KL | 1
R4,R5,R32 | RT0805DRD0733KL | 3
R6,R33,R34 | SG73G2ATTD1002D | 3
R7 | SG73G2ATTD1004D | 1
R8 | SG73G2ATTD1001D | 1
R9 | RT0805DRE07120KL | 1
RTC_BAT1 | S8401-46 | 1
RV1 |  | 1
SW2 | 100SP5T4B4VS2QE | 1
SW3-SW5 | KSL0A411LFTR | 3
TP1 |  | 1
TP10 |  | 1
TP11 |  | 1
TP12 |  | 1
TP13 |  | 1
TP14 |  | 1
TP15 |  | 1
TP16 |  | 1
TP2 |  | 1
TP3 |  | 1
TP4 |  | 1
TP5 |  | 1
TP6 |  | 1
TP7 |  | 1
TP8 |  | 1
TP9 |  | 1
U1 | LM358LVIDGKR | 1
U10 | MPXV5050GP | 1
U2 | 4N35 | 1
U3 | LCD-10168 | 1
U4 | LM8364BALMF20/NOPB | 1
U5,U11 | BAV199HMFHT116 | 2
U6 | LM2575-3.3WU | 1
U7 | LM2940IMP-5.0/NOPB | 1
U8 | LPC1769FBD100 | 1
U9 | 24LC64-I/SN | 1
Y1 | ABM3B-12.000MHZ-B2-T | 1
Y2 | TFE202W32K7680R | 1

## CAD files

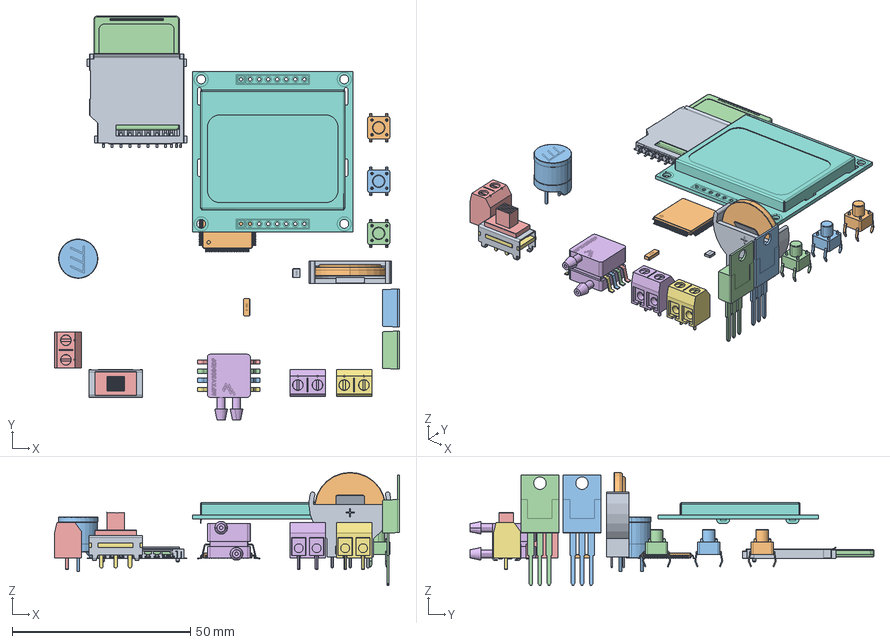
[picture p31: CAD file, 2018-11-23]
pcb/TensiometroDigital/GABINETE/pcb.fcstd
96.7 x 113.2 x 31.7 mm
socket_a-sd-09-c-0-7-3
SW3dPS-LQFP100
Coilcraft-RFC1010B
SDDEFAU0405151505845
alsrobot-SW SPDT
alsrobot-SW SPDT001
alsrobot-SW SPDT002
alsrobot-SW SPDT003
alsrobot-SW SPDT004
DIDEFAU01121457272363
DIDEFAU01121457272364
DIDEFAU01121457272365
User Library-ABM10_Xtal
User Library-ABM10_Xtal001
User Library-ABM10_Xtal002
User Library-ABM10_Xtal003
User Library-ABM10_Xtal004
User Library-ASB 10
User Library-Bornera
User Library-Bornera001
User Library-Bornera002
User Library-CR2032 Battery Holder-Dip180
User Library-CR2032 Battery Holder-Dip181
SW3DPS-BATT CR2032-DEFAULT
User Library-MPXV5004DP
User Library-MPXV5004DP001
User Library-MPXV5004DP002
User Library-MPXV5004DP003
User Library-MPXV5004DP004
User Library-LCD5110R-1

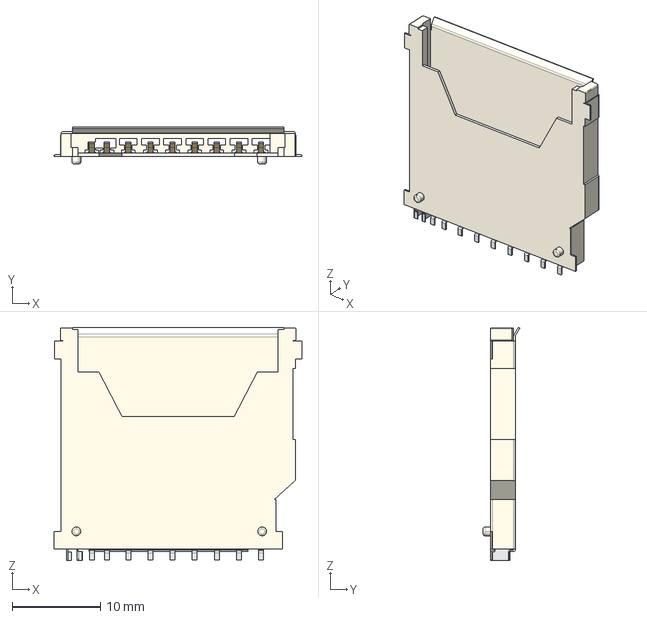
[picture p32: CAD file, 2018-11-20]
pcb/TensiometroDigital/shapes3D/80096902-3-socket_a-sd-09-c-0-7-3/socket_a-sd-09-c-0-7-3.stp
28.0 x 4.15 x 26.4 mm

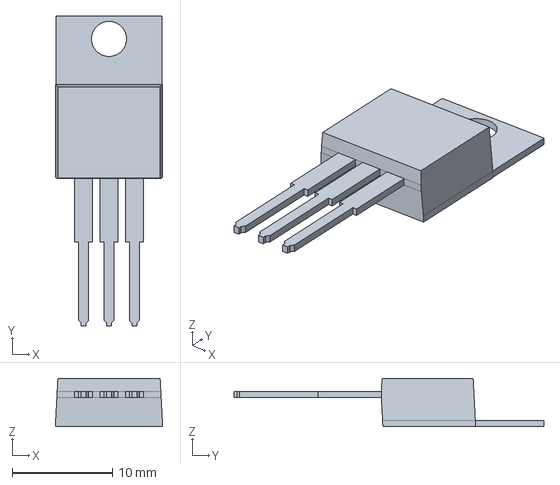
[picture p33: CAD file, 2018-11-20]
pcb/TensiometroDigital/shapes3D/80127368-3-tip31cg/tip31cg.stp
10.7 x 31.0 x 4.83 mm

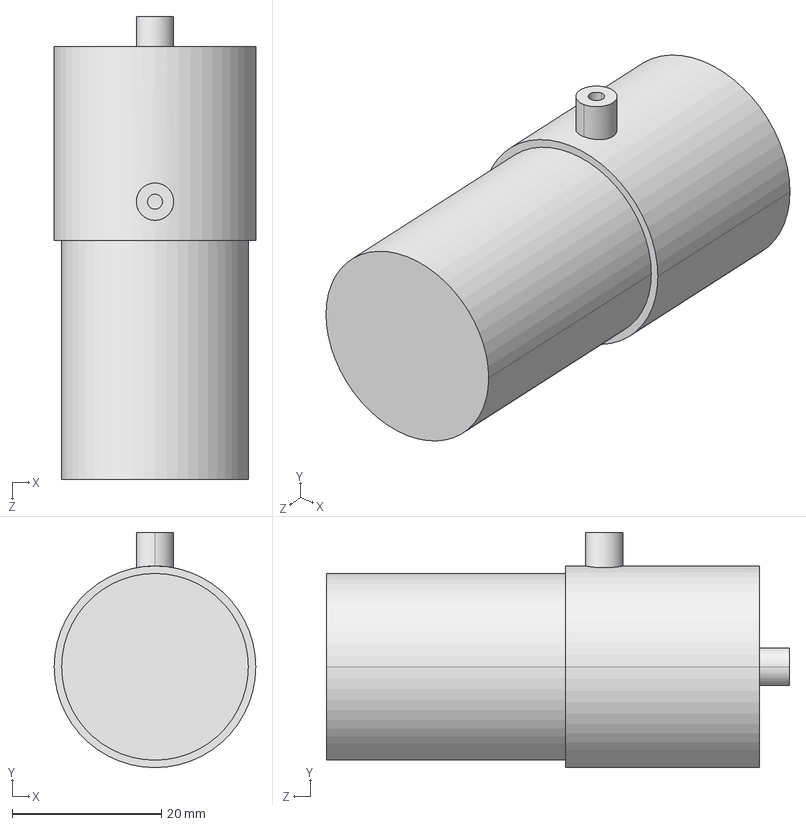
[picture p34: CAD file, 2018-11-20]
pcb/TensiometroDigital/shapes3D/User Library-air pump.STEP
27.0 x 31.5 x 62.0 mm

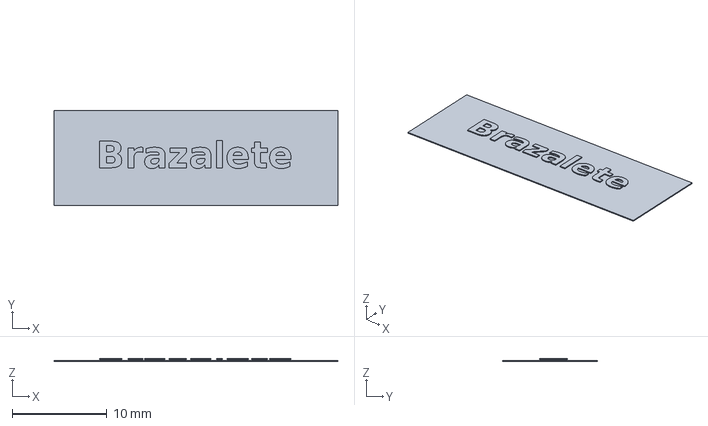
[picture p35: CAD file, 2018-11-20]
pcb/TensiometroDigital/GABINETE/etiquetas.fcstd
30.0 x 10.0 x 0.3 mm

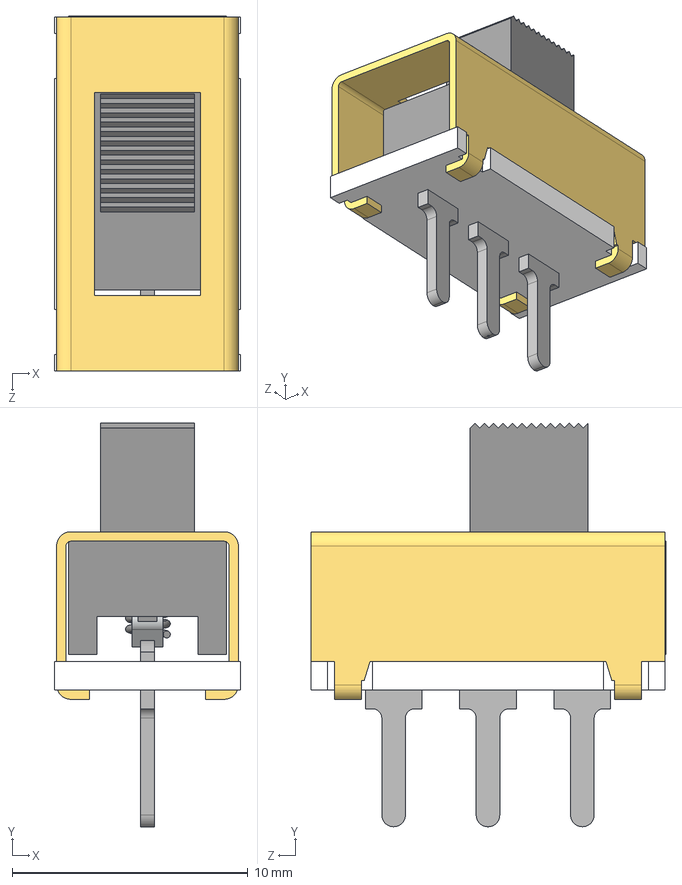
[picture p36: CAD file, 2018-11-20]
pcb/TensiometroDigital/shapes3D/alsrobot-SW SPDT.STEP
7.90 x 17.1 x 15.0 mm
alsrobot-SW SPDT_User Library-chave_mini_H-H_alavanca_chave_mini_H-H_alavanca_botao_baixo_Valor predeterminado
alsrobot-SW SPDT_User Library-chave_mini_H-H_alavanca_chave_mini_H-H_alavanca_contato_Valor predeterminado
alsrobot-SW SPDT_User Library-chave_mini_H-H_alavanca_chave_mini_H-H_alavanca_base_3_pinos_PCB_Valor predeterminado
alsrobot-SW SPDT_User Library-chave_mini_H-H_alavanca_chave_mini_H-H_alavanca_mola_Valor predeterminado
alsrobot-SW SPDT_User Library-chave_mini_H-H_alavanca_chave_mini_H-H_alavanca_corpo_sem_abas_Valor predeterminado

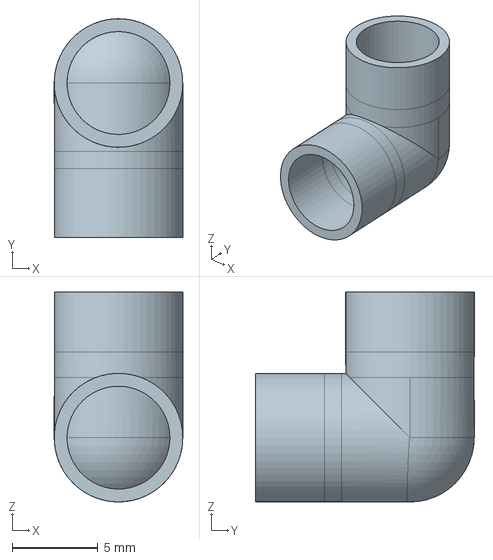
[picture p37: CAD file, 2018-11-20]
pcb/TensiometroDigital/GABINETE/manguera.fcstd
7.50 x 12.7 x 12.2 mm

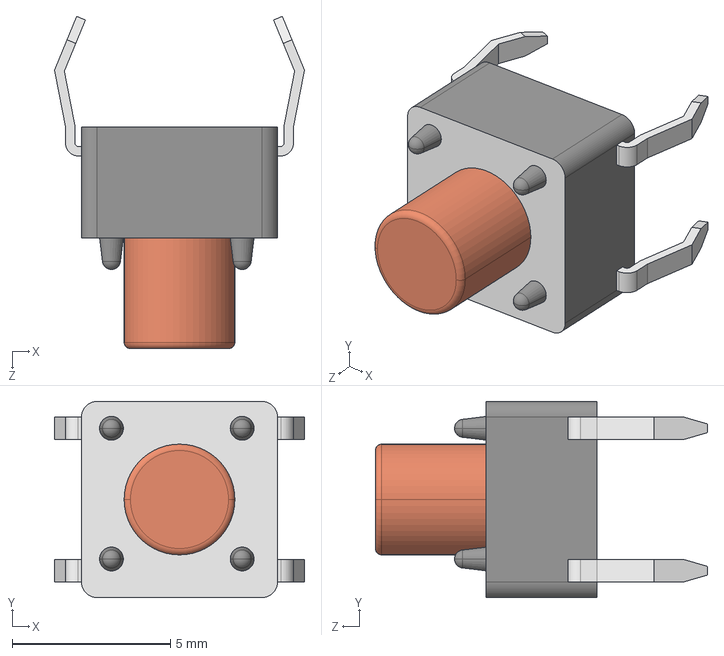
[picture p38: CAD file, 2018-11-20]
pcb/TensiometroDigital/shapes3D/SW3dPS-diptronics tactile dts-63k.STEP
7.90 x 6.20 x 10.5 mm

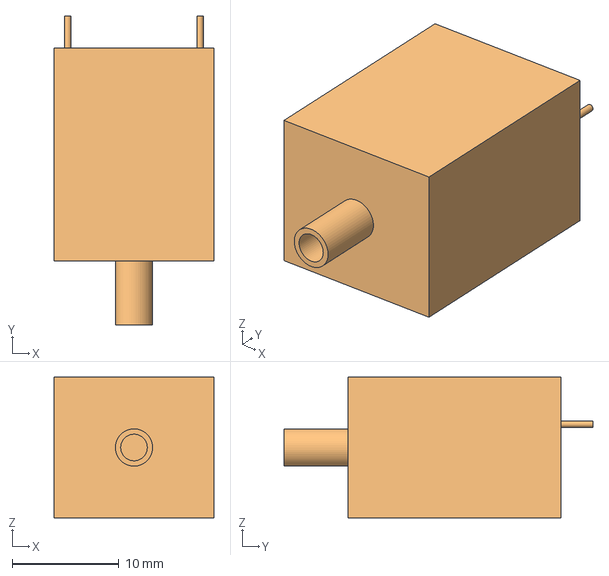
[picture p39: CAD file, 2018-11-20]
pcb/TensiometroDigital/GABINETE/valvula.fcstd
15.0 x 29.0 x 13.2 mm
valve

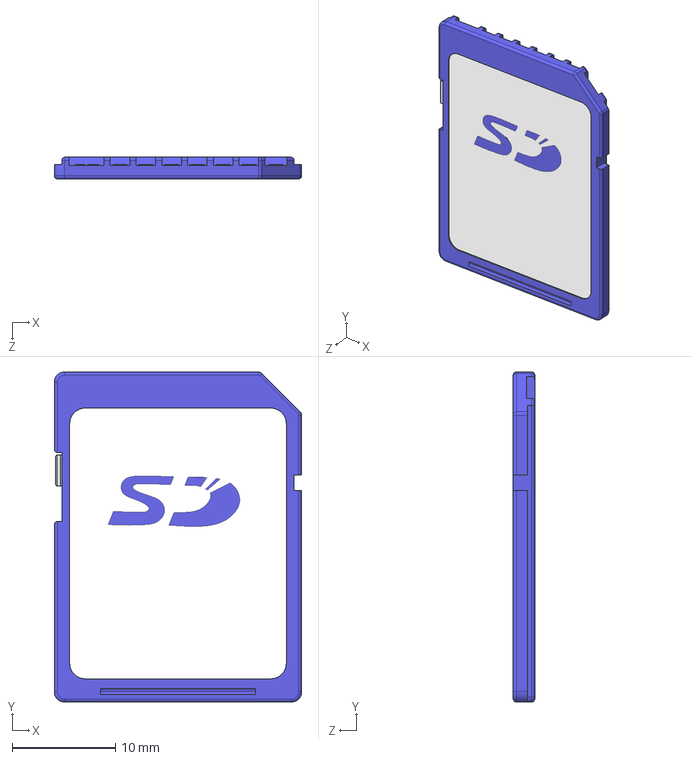
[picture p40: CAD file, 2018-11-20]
pcb/TensiometroDigital/shapes3D/SW3dPS-sd card.STEP
24.0 x 32.0 x 2.10 mm

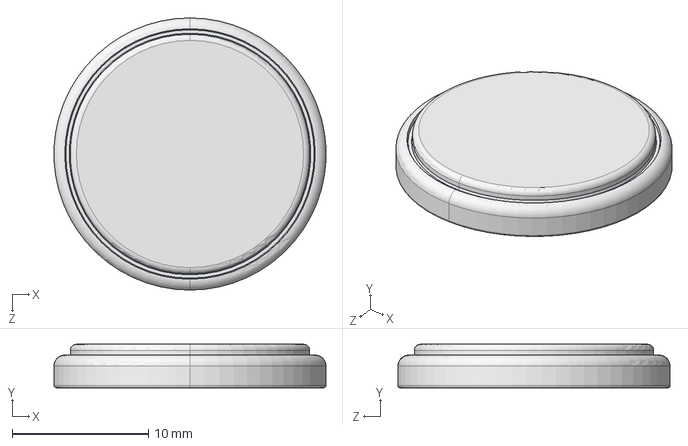
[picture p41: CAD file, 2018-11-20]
pcb/TensiometroDigital/shapes3D/SW3DPS-BATT CR2032-DEFAULT.STEP
20.0 x 3.20 x 20.0 mm

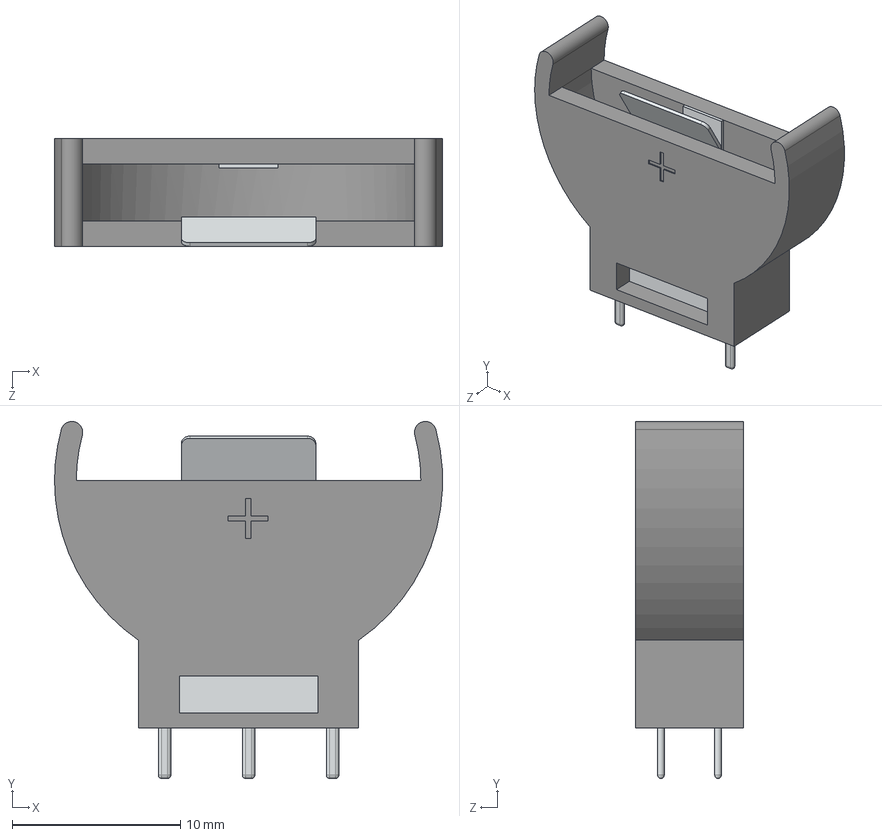
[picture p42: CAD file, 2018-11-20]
pcb/TensiometroDigital/shapes3D/User Library-CR2032 Battery Holder-Dip180.STEP
23.1 x 21.2 x 6.40 mm

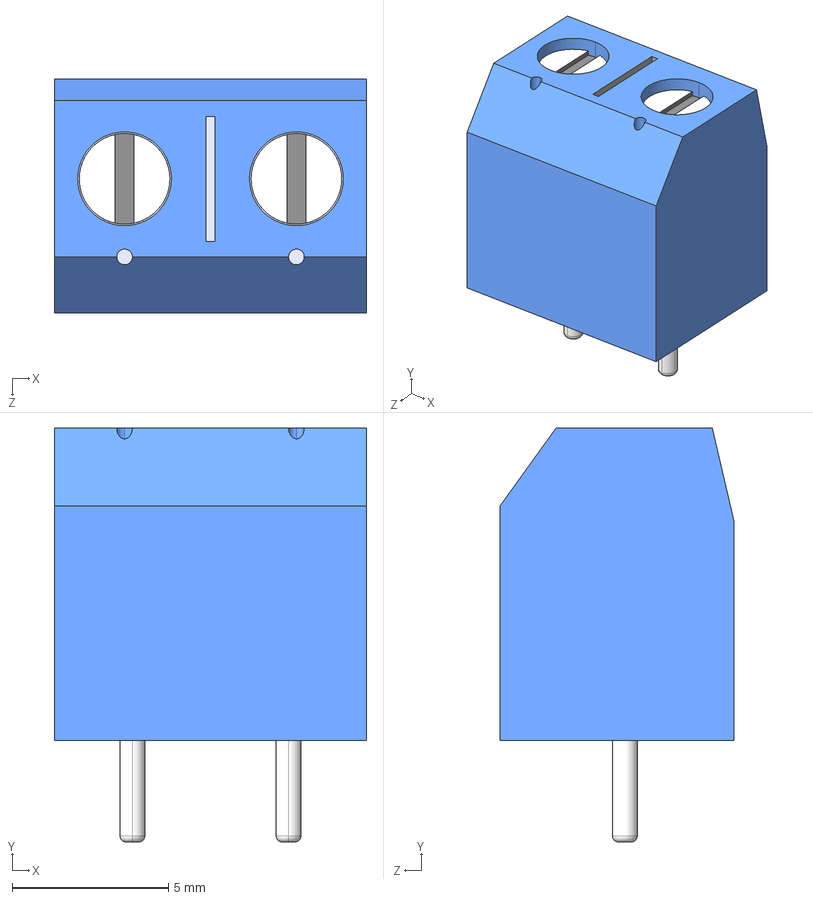
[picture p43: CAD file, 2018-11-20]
pcb/TensiometroDigital/shapes3D/User Library-Bornera.STEP
10.0 x 13.3 x 7.50 mm

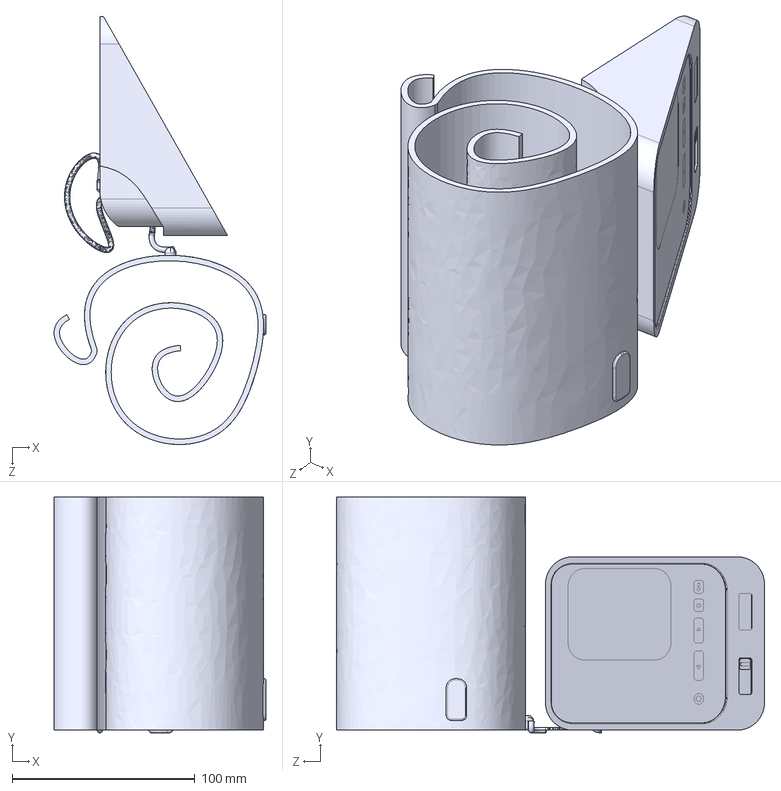
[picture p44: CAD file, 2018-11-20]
pcb/TensiometroDigital/shapes3D/User Library-OMRON.STEP
116.1 x 129.3 x 234.5 mm

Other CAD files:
pcb/TensiometroDigital/shapes3D/SW3dPS-LQFP100.STEP
pcb/TensiometroDigital/shapes3D/User Library-ASB 10.STEP
pcb/TensiometroDigital/shapes3D/SW3DPS-LED DIP 3MM-DEFAULT.STEP
pcb/TensiometroDigital/shapes3D/User Library-Header1x2.STEP
pcb/TensiometroDigital/shapes3D/80180752-3-70746593/70746593.stp
pcb/TensiometroDigital/shapes3D/80181900-3-41812/41812.stp
pcb/TensiometroDigital/shapes3D/Coilcraft-RFC1010B.STEP
pcb/TensiometroDigital/shapes3D/User Library-18650 holder x2.STEP
pcb/TensiometroDigital/shapes3D/User Library-3-way Elbow Furniture Grade PVC Fitting Connector.STEP
pcb/TensiometroDigital/shapes3D/User Library-90 degree elbow bspt.STEP
pcb/TensiometroDigital/shapes3D/User Library-ABM10_Xtal.STEP
pcb/TensiometroDigital/shapes3D/User Library-IRC18650-1.STEP
pcb/TensiometroDigital/shapes3D/User Library-M3x0_5xL Phillips Panhead Screw.STEP
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

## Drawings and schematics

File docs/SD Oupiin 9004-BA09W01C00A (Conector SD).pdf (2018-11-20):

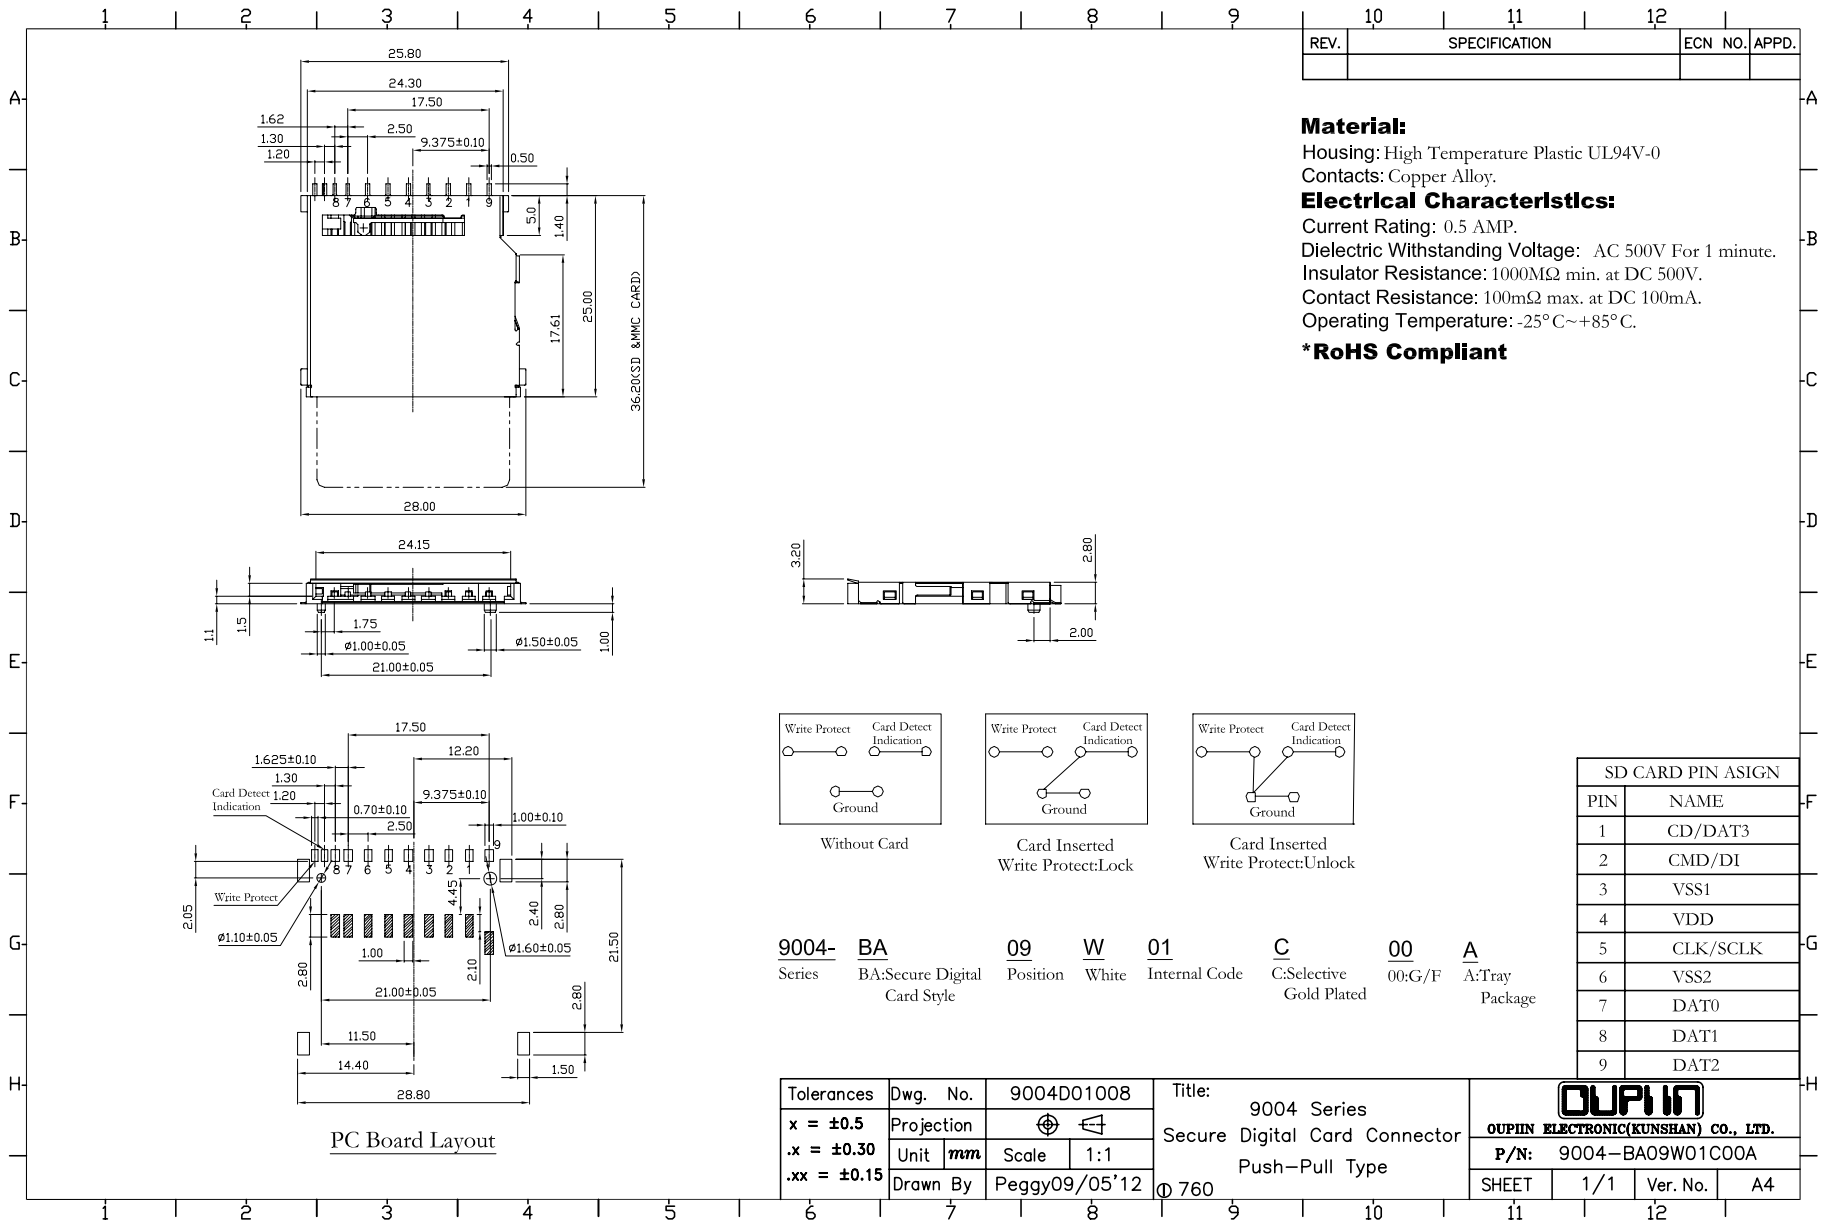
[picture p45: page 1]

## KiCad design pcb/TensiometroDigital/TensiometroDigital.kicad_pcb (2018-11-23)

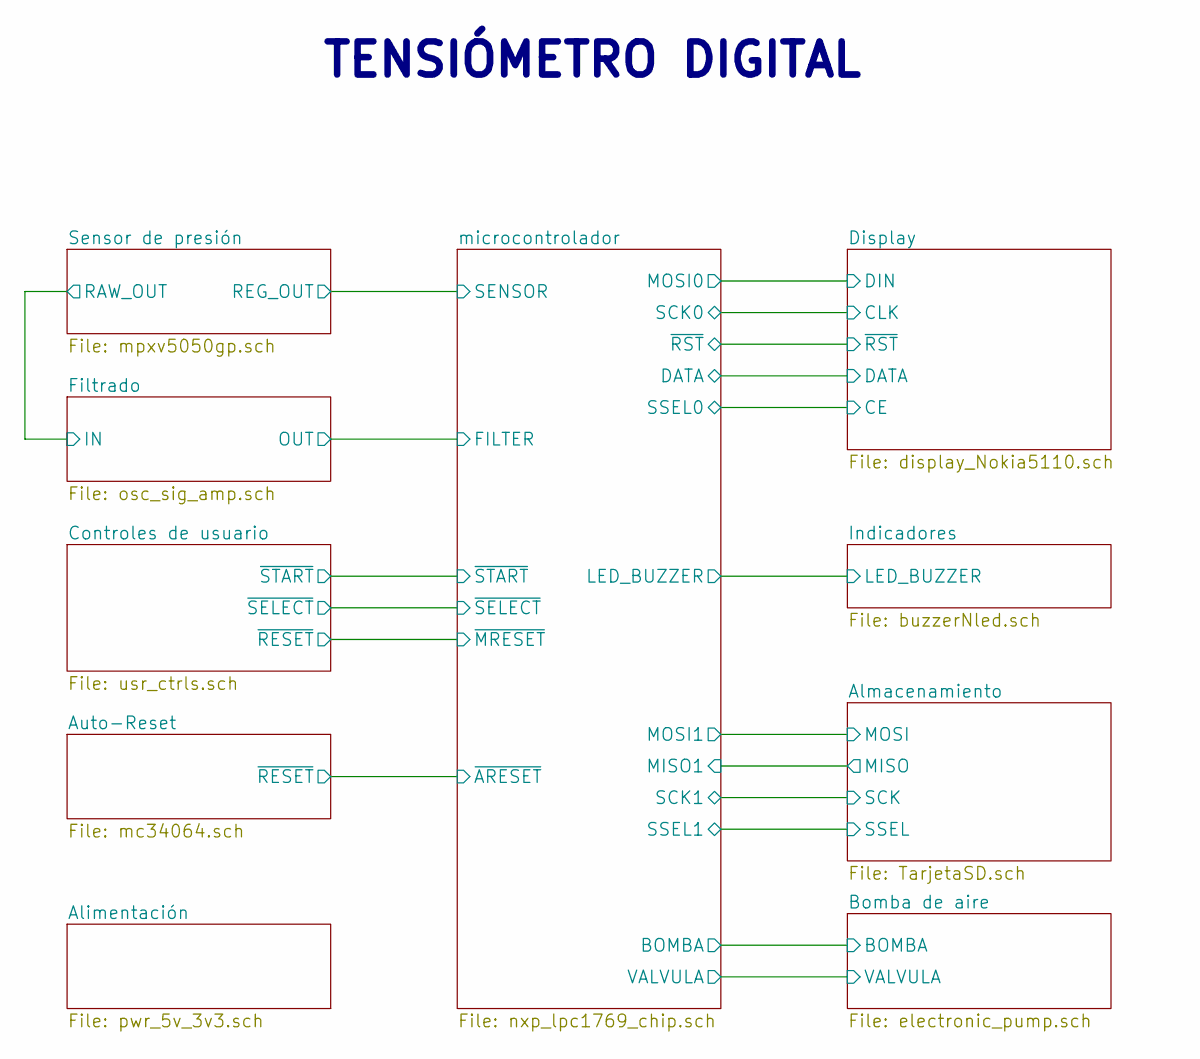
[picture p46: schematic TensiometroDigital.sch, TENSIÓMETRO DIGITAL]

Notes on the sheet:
TENSIÓMETRO DIGITAL

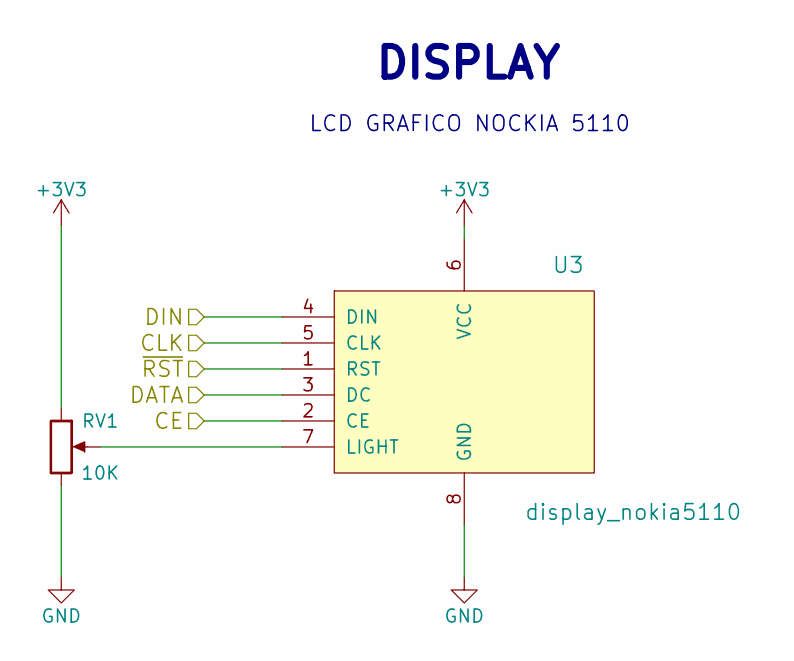
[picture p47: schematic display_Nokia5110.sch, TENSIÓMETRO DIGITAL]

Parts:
RV1: 10K; Potentiometer_Trimmer_Bourns_3296W
U3: display_nokia5110; Socket_Strip_Straight_1x08_Pitch2.54mm

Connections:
/Display/CE: U3.2 (CE); also elsewhere on the board
/Display/CLK: U3.5 (CLK); also elsewhere on the board
/Display/DATA: U3.3 (DC); also elsewhere on the board
/Display/DIN: U3.4 (DIN); also elsewhere on the board
/Display/~RST: U3.1 (RST); also elsewhere on the board
GND: RV1.3, U3.8 (GND); also elsewhere on the board
unnamed: RV1.2, U3.7 (LIGHT)

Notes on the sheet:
LCD GRAFICO NOCKIA 5110
DISPLAY

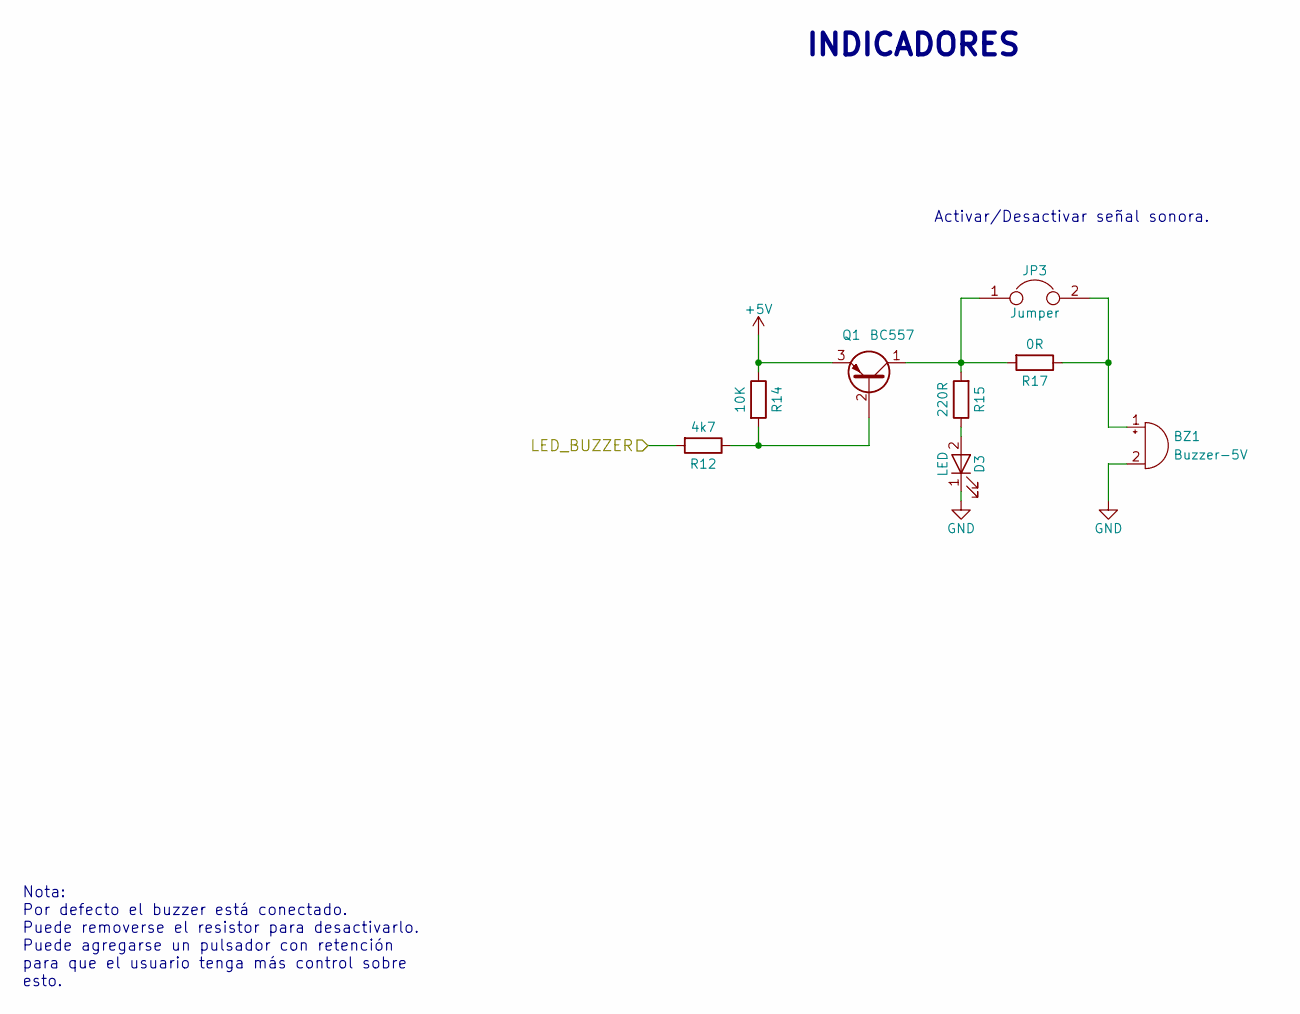
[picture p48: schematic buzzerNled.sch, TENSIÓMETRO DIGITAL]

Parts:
BZ1: Buzzer-5V; Buzzer_12x9.5RM7.6
D3: LED; LED_D3.0mm
JP3: Jumper; Socket_Strip_Straight_1x02_Pitch2.54mm
Q1: BC557; TO-92_Molded_Narrow
R12: 4k7; R_0805_HandSoldering
R14: 10K; R_0805_HandSoldering
R15: 220R; R_0805_HandSoldering
R17: 0R; R_0805_HandSoldering

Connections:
+5V: Q1.3 (E), R14.1; also elsewhere on the board
/Indicadores/LED_BUZZER: R12.2; also elsewhere on the board
GND: BZ1.2 (+), D3.1 (K); also elsewhere on the board
unnamed: BZ1.1 (-), JP3.2, R17.1
unnamed: D3.2 (A), R15.1
unnamed: JP3.1, Q1.1 (C), R15.2, R17.2
unnamed: Q1.2 (B), R12.1, R14.2

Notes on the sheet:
INDICADORES
Activar/Desactivar señal sonora.
Nota: Por defecto el buzzer está conectado. Puede removerse el resistor para desactivarlo. Puede agregarse un pulsador con retención para que el usuario tenga más control sobre esto.

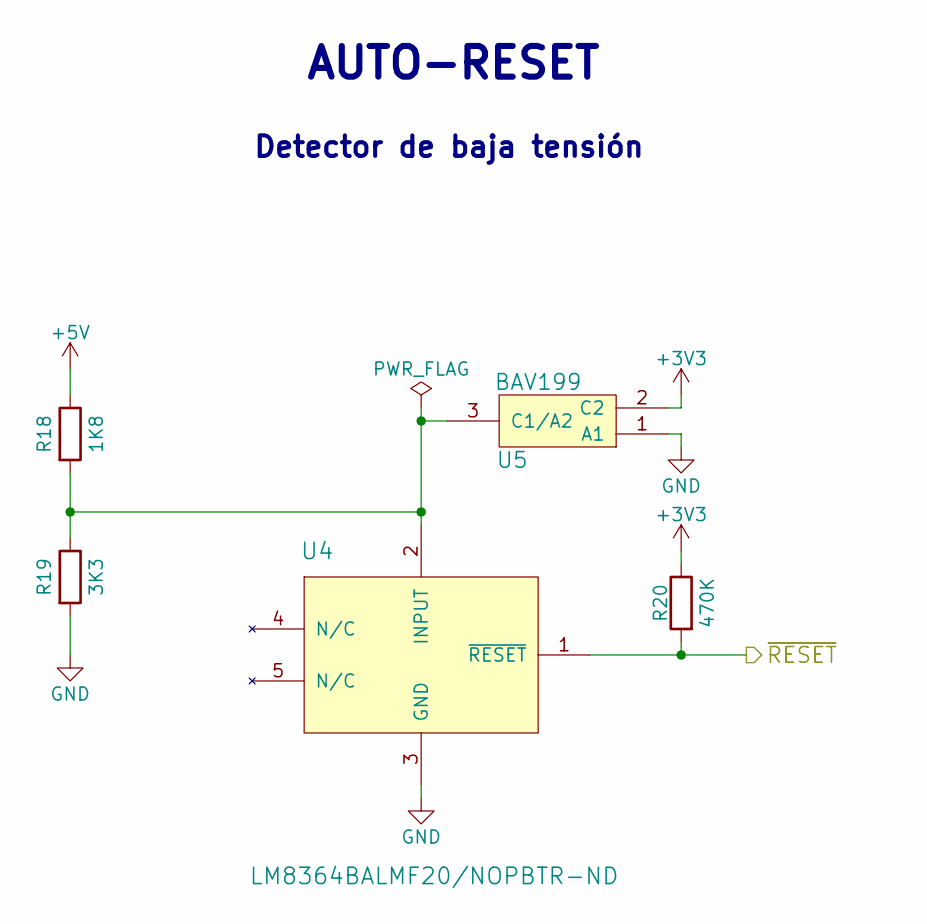
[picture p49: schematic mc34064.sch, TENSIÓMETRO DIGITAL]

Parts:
R18: 1K8; R_0805_HandSoldering
R19: 3K3; R_0805_HandSoldering
R20: 470K; R_0805_HandSoldering
U4: LM8364BALMF20/NOPBTR-ND; SOT-23-5_HandSoldering
U5: BAV199; SOT-23

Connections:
+5V: R18.1; also elsewhere on the board
/microcontrolador/~ARESET: R20.2, U4.1 (~RESET); also elsewhere on the board
GND: R19.2, U4.3 (GND), U5.1 (A1); also elsewhere on the board
unnamed: R18.2, R19.1, U4.2 (INPUT), U5.3 (C1/A2)

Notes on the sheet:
AUTO-RESET
Detector de baja tensión

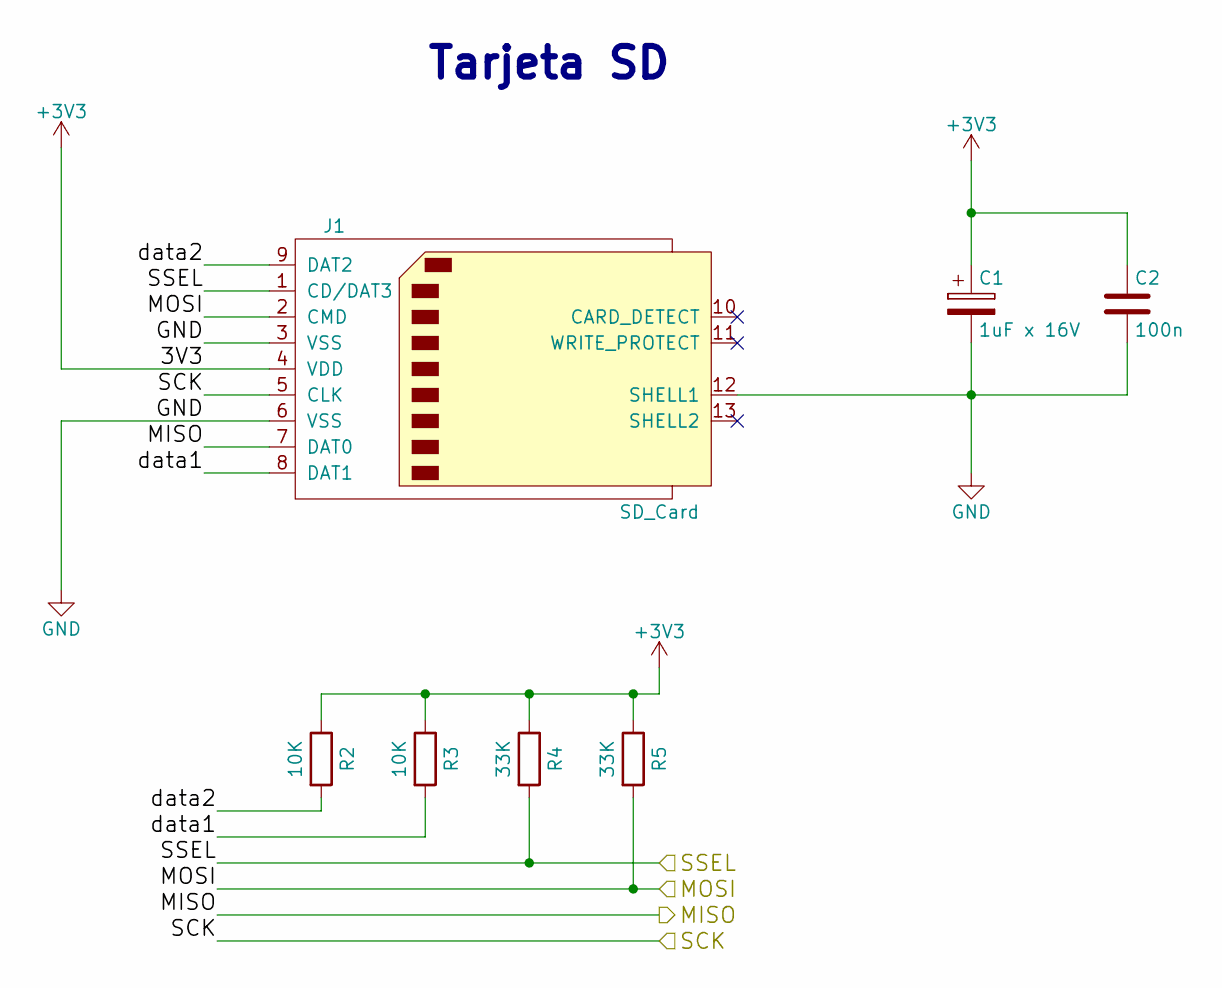
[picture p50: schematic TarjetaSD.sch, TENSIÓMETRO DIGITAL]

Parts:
C1: 1uF x 16V; CP_Tantalum_Case-A_EIA-3216-18_Hand
C2: 100n; C_0805_HandSoldering
J1: SD_Card; SD_TE_2041021_edit
R2, R3: 10K; R_0805_HandSoldering
R4, R5: 33K; R_0805_HandSoldering

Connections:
/Almacenamiento/MISO: J1.7 (DAT0); also elsewhere on the board
/Almacenamiento/MOSI: J1.2 (CMD), R5.2; also elsewhere on the board
/Almacenamiento/SCK: J1.5 (CLK); also elsewhere on the board
/Almacenamiento/SSEL: J1.1 (CD/DAT3), R4.2; also elsewhere on the board
/Almacenamiento/data1: J1.8 (DAT1), R3.2
/Almacenamiento/data2: J1.9 (DAT2), R2.2
GND: C1.2, C2.2, J1.3 (VSS), J1.6 (VSS), J1.12 (SHELL1); also elsewhere on the board

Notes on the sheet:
Tarjeta SD

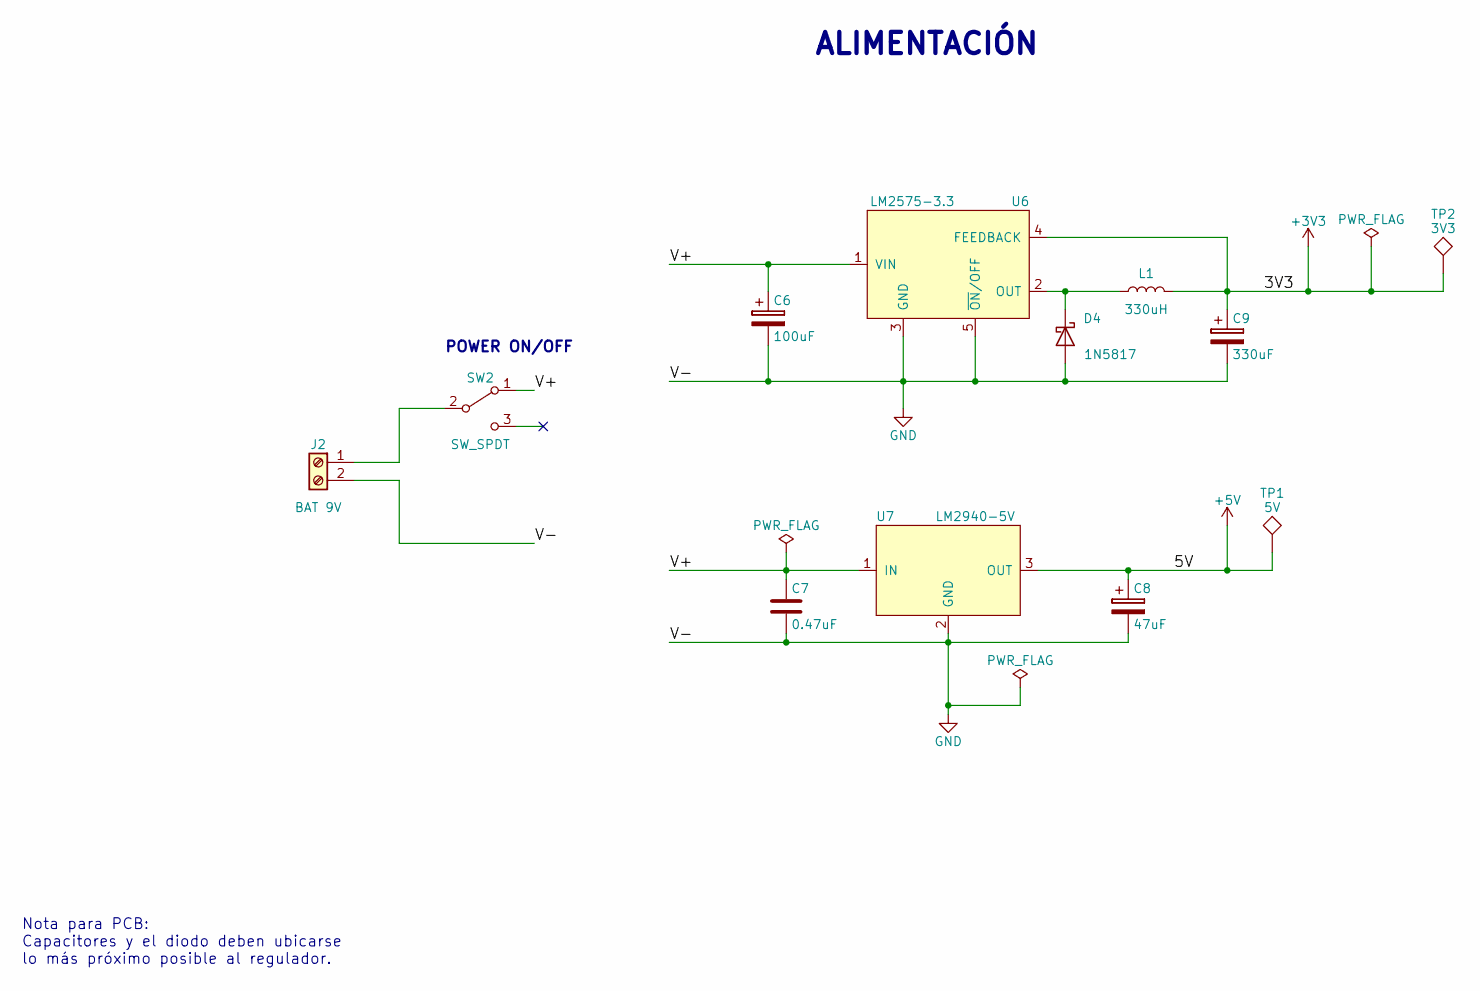
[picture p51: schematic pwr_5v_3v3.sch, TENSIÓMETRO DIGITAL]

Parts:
C6: 100uF; CP_Elec_6.3x5.8
C7: 0.47uF; CP_Elec_4x5.7
C8: 47uF; CP_Elec_6.3x4.5
C9: 330uF; CP_Elec_6.3x7.7
D4: 1N5817; D_DO-41_SOD81_P10.16mm_Horizontal
J2: BAT 9V; TerminalBlock_bornier-2_P5.08mm
L1: 330uH; RFC1010
SW2: SW_SPDT; E_SWITCH_100SP5T4B4VS2QE
TP1: 5V; TestPoint_THTPad_D1.5mm_Drill0.7mm
TP2: 3V3; TestPoint_THTPad_D1.5mm_Drill0.7mm
U6: LM2575-3.3; TO-263-5_TabPin3
U7: LM2940-5V; SOT-223-3_TabPin2

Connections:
+5V: C8.1, TP1.1, U7.3 (OUT); also elsewhere on the board
/Alimentación/V+: C6.1, C7.1, SW2.1 (A), U6.1 (VIN), U7.1 (IN)
GND: C6.2, C7.2, C8.2, C9.2, D4.2 (A), J2.2, U6.3 (GND), U6.5 (~ON~/OFF), U7.2 (GND); also elsewhere on the board
unnamed: D4.1 (K), L1.1, U6.2 (OUT)
unnamed: J2.1, SW2.2 (B)

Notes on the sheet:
ALIMENTACIÓN
Nota para PCB: Capacitores y el diodo deben ubicarse lo más próximo posible al regulador.
POWER ON/OFF

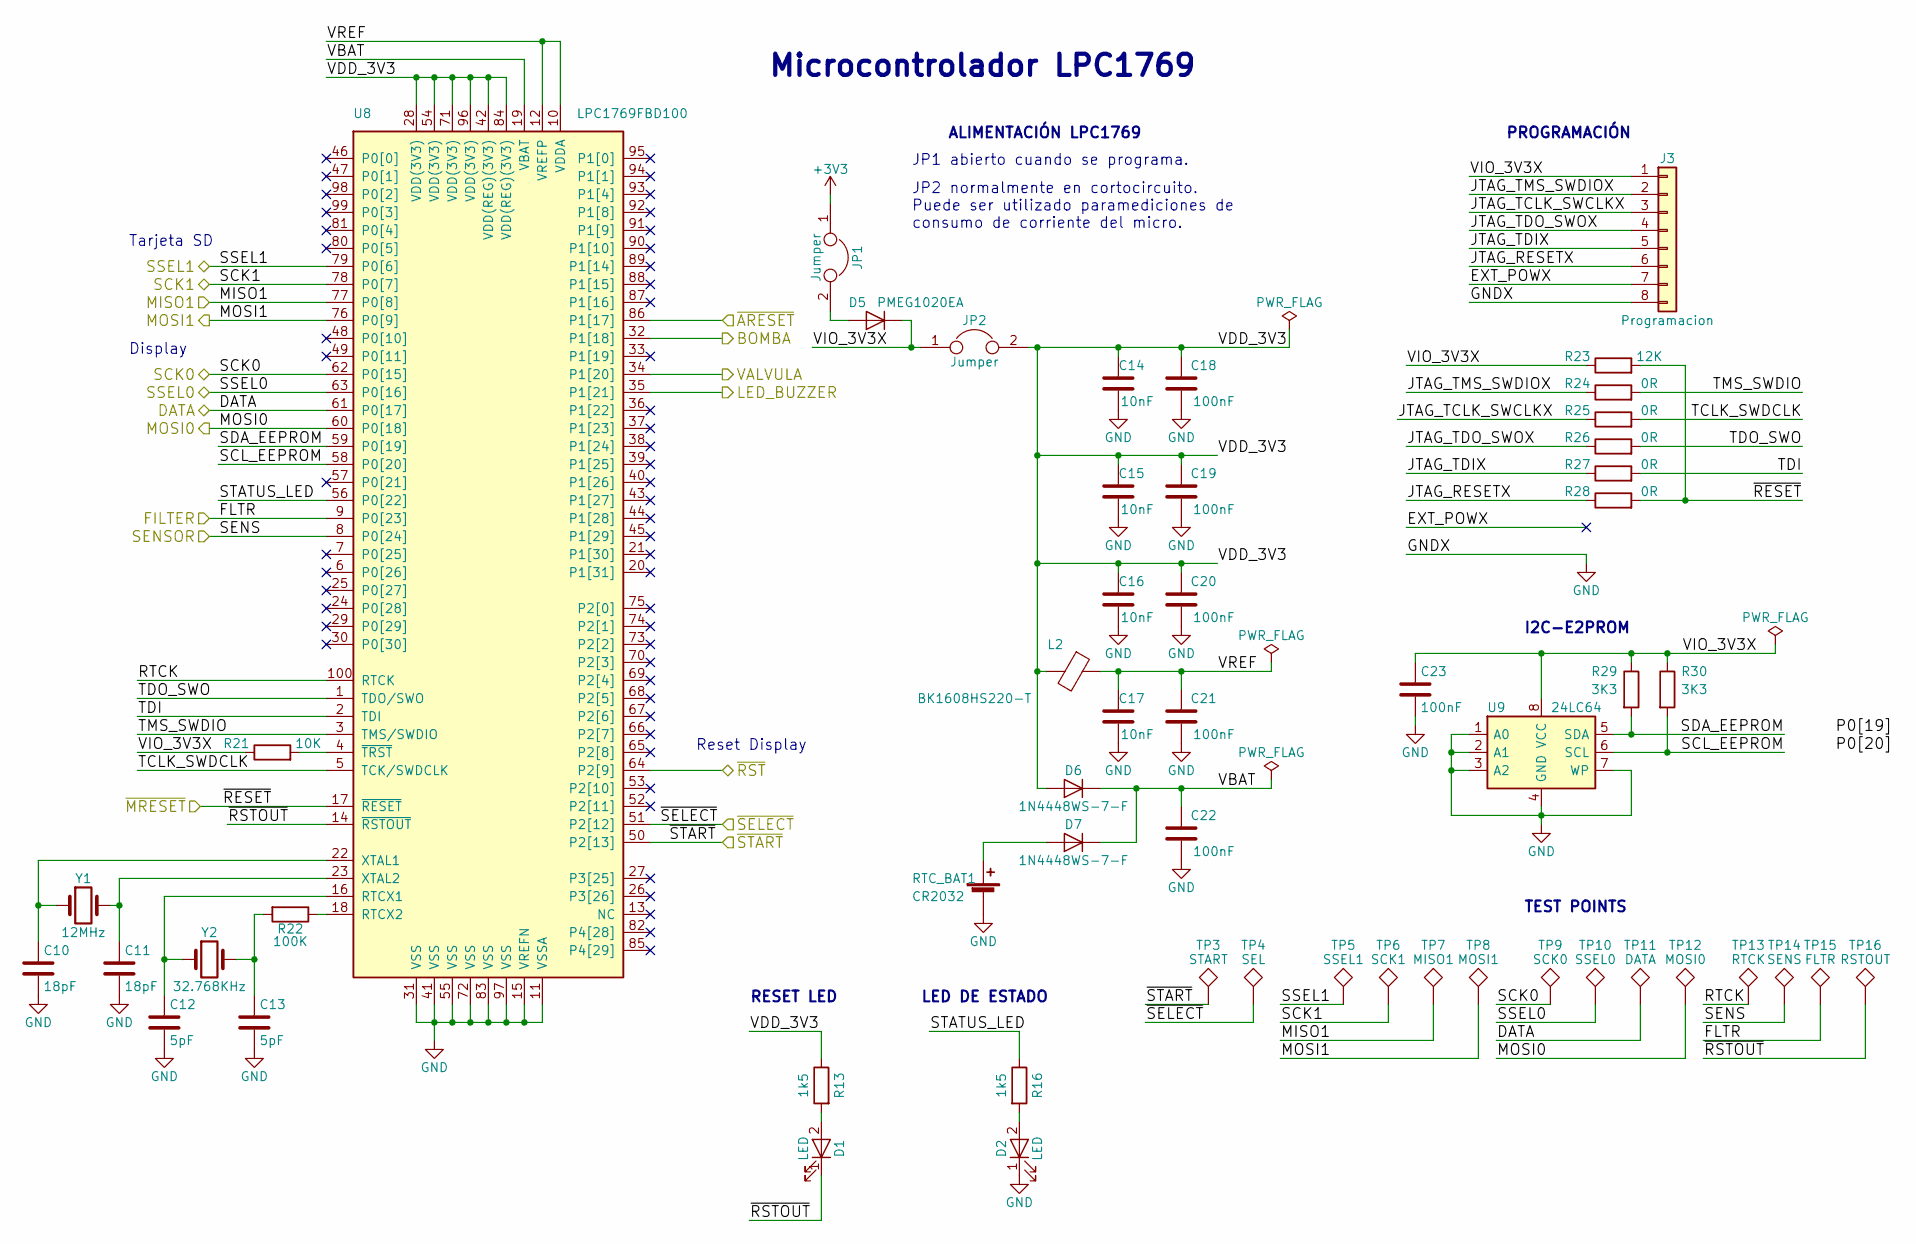
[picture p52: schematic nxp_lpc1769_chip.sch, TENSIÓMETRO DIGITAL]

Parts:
C10, C11: 18pF; C_0805_HandSoldering
C12, C13: 5pF; C_0805_HandSoldering
C14, C15, C16, C17: 10nF; C_0805_HandSoldering
C18, C19, C20, C21, C22, C23: 100nF; C_0805_HandSoldering
D1, D2: LED; LED_0402
D5: PMEG1020EA; D_SOD-323
D6, D7: 1N4448WS-7-F; D_SOD-323
J3: Programacion; Socket_Strip_Straight_1x08_Pitch2.54mm
JP1, JP2: Jumper; Socket_Strip_Straight_1x02_Pitch2.54mm
L2: BK1608HS220-T; L_0603_HandSoldering
R13, R16: 1k5; R_0805_HandSoldering
R21: 10K; R_0805_HandSoldering
R22: 100K; R_0805_HandSoldering
R23: 12K; R_0805_HandSoldering
R24, R25, R26, R27, R28: 0R; R_0805_HandSoldering
R29, R30: 3K3; R_0805_HandSoldering
RTC_BAT1: CR2032; CR2032_VERTICAL_HOLDER_S8401-46
TP3: START; TestPoint_THTPad_D1.5mm_Drill0.7mm
TP4: SEL; TestPoint_THTPad_D1.5mm_Drill0.7mm
TP5: SSEL1; TestPoint_THTPad_D1.5mm_Drill0.7mm
TP6: SCK1; TestPoint_THTPad_D1.5mm_Drill0.7mm
TP7: MISO1; TestPoint_THTPad_D1.5mm_Drill0.7mm
TP8: MOSI1; TestPoint_THTPad_D1.5mm_Drill0.7mm
TP9: SCK0; TestPoint_THTPad_D1.5mm_Drill0.7mm
TP10: SSEL0; TestPoint_THTPad_D1.5mm_Drill0.7mm
TP11: DATA; TestPoint_THTPad_D1.5mm_Drill0.7mm
TP12: MOSI0; TestPoint_THTPad_D1.5mm_Drill0.7mm
TP13: RTCK; TestPoint_THTPad_D1.5mm_Drill0.7mm
TP14: SENS; TestPoint_THTPad_D1.5mm_Drill0.7mm
TP15: FLTR; TestPoint_THTPad_D1.5mm_Drill0.7mm
TP16: RSTOUT; TestPoint_THTPad_D1.5mm_Drill0.7mm
U8: LPC1769FBD100; LQFP-100_14x14mm_P0.5mm
U9: 24LC64; SOIC-8_3.9x4.9mm_Pitch1.27mm
Y1: 12MHz; Crystal_SMD_Abracon_ABM3C-4pin_5.0x3.2mm
Y2: 32.768KHz; Crystal_SMD_2012-2pin_2.0x1.2mm_HandSoldering

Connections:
/Almacenamiento/MISO: TP7.1, U8.77 (P0[8]); also elsewhere on the board
/Almacenamiento/MOSI: TP8.1, U8.76 (P0[9]); also elsewhere on the board
/Almacenamiento/SCK: TP6.1, U8.78 (P0[7]); also elsewhere on the board
/Almacenamiento/SSEL: TP5.1, U8.79 (P0[6]); also elsewhere on the board
/Bomba de aire/BOMBA: U8.32 (P1[18]); also elsewhere on the board
/Bomba de aire/VALVULA: U8.34 (P1[20]); also elsewhere on the board
/Controles de usuario/~SELECT: TP4.1, U8.51 (P2[12]); also elsewhere on the board
/Controles de usuario/~START: TP3.1, U8.50 (P2[13]); also elsewhere on the board
/Display/CE: TP10.1, U8.63 (P0[16]); also elsewhere on the board
/Display/CLK: TP9.1, U8.62 (P0[15]); also elsewhere on the board
/Display/DATA: TP11.1, U8.61 (P0[17]); also elsewhere on the board
/Display/DIN: TP12.1, U8.60 (P0[18]); also elsewhere on the board
/Display/~RST: U8.64 (P2[9]); also elsewhere on the board
/Indicadores/LED_BUZZER: U8.35 (P1[21]); also elsewhere on the board
/Sensor de presión/REG_OUT: TP14.1, U8.8 (P0[24]); also elsewhere on the board
/microcontrolador/EXT_POWX: J3.7
/microcontrolador/FILTER: TP15.1, U8.9 (P0[23]); also elsewhere on the board
/microcontrolador/JTAG_RESETX: J3.6, R28.1
/microcontrolador/JTAG_TCLK_SWCLKX: J3.3, R25.1
/microcontrolador/JTAG_TDIX: J3.5, R27.1
/microcontrolador/JTAG_TDO_SWOX: J3.4, R26.1
/microcontrolador/JTAG_TMS_SWDIOX: J3.2, R24.1
/microcontrolador/RTCK: TP13.1, U8.100 (RTCK)
/microcontrolador/SCL_EEPROM: R30.2, U8.58 (P0[20]), U9.6 (SCL)
/microcontrolador/SDA_EEPROM: R29.2, U8.59 (P0[19]), U9.5 (SDA)
/microcontrolador/STATUS_LED: R16.1, U8.56 (P0[22])
/microcontrolador/TCLK_SWDCLK: R25.2, U8.5 (TCK/SWDCLK)
/microcontrolador/TDI: R27.2, U8.2 (TDI)
/microcontrolador/TDO_SWO: R26.2, U8.1 (TDO/SWO)
/microcontrolador/TMS_SWDIO: R24.2, U8.3 (TMS/SWDIO)
/microcontrolador/VBAT: C22.1, D6.1 (K), D7.1 (K), U8.19 (VBAT)
/microcontrolador/VDD_3V3: C14.1, C15.1, C16.1, C18.1, C19.1, C20.1, D6.2 (A), JP2.2, L2.2, R13.1, U8.28 (VDD(3V3)), U8.42 (VDD(REG)(3V3)), U8.54 (VDD(3V3)), U8.71 (VDD(3V3)), U8.84 (VDD(REG)(3V3)), U8.96 (VDD(3V3))
/microcontrolador/VIO_3V3X: C23.1, D5.1 (K), J3.1, JP2.1, R21.1, R23.1, R29.1, R30.1, U9.8 (VCC)
/microcontrolador/VREF: C17.1, C21.1, L2.1, U8.10 (VDDA), U8.12 (VREFP)
/microcontrolador/~ARESET: U8.86 (P1[17]); also elsewhere on the board
/microcontrolador/~MRESET: R23.2, R28.2, U8.17 (~RESET~); also elsewhere on the board
/microcontrolador/~RSTOUT: D1.1 (K), TP16.1, U8.14 (~RSTOUT~)
GND: C10.2, C11.2, C12.2, C13.2, C14.2, C15.2, C16.2, C17.2, C18.2, C19.2, C20.2, C21.2, C22.2, C23.2, D2.1 (K), J3.8, RTC_BAT1.2 (-), U8.11 (VSSA), U8.15 (VREFN), U8.31 (VSS), U8.41 (VSS), U8.55 (VSS), U8.72 (VSS), U8.83 (VSS), U8.97 (VSS), U9.1 (A0), U9.2 (A1), U9.3 (A2), U9.4 (GND), U9.7 (WP); also elsewhere on the board
unnamed: C10.1, U8.22 (XTAL1), Y1.1
unnamed: C11.1, U8.23 (XTAL2), Y1.2
unnamed: C12.1, U8.16 (RTCX1), Y2.1
unnamed: C13.1, R22.2, Y2.2
unnamed: D1.2 (A), R13.2
unnamed: D2.2 (A), R16.2
unnamed: D5.2 (A), JP1.2
unnamed: D7.2 (A), RTC_BAT1.1 (+)
unnamed: R21.2, U8.4 (~TRST~)
unnamed: R22.1, U8.18 (RTCX2)

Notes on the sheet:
Microcontrolador LPC1769
PROGRAMACIÓN
I2C-E2PROM
JP2 normalmente en cortocircuito. Puede ser utilizado paramediciones de consumo de corriente del micro.
JP1 abierto cuando se programa.
ALIMENTACIÓN LPC1769
Reset Display
Tarjeta SD
Display
TEST POINTS
RESET LED
LED DE ESTADO

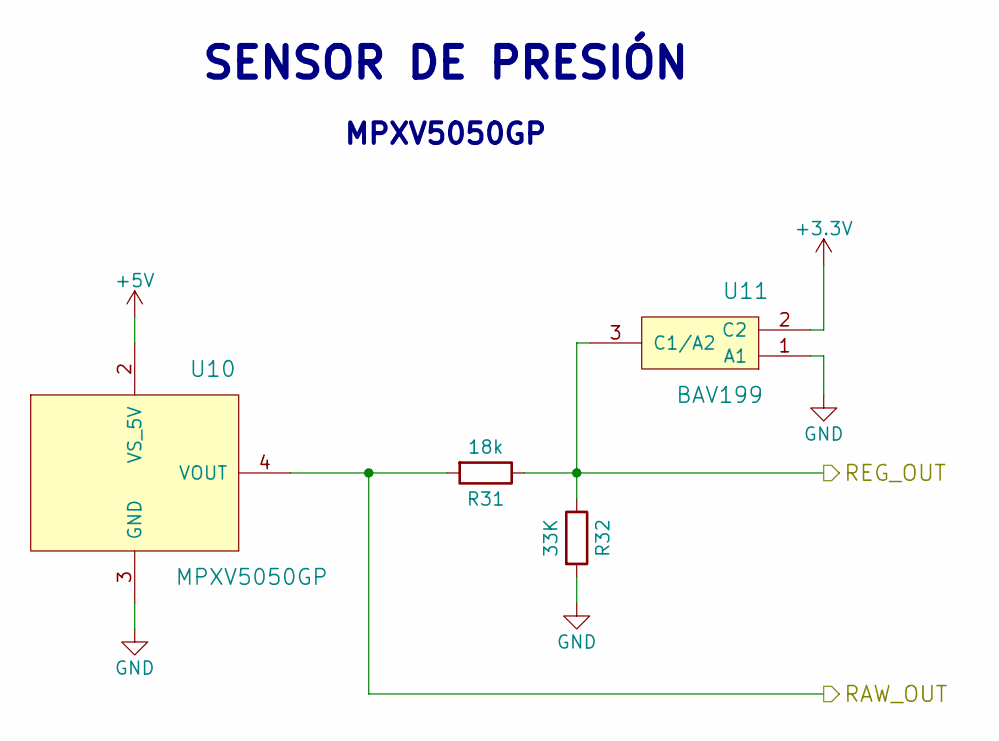
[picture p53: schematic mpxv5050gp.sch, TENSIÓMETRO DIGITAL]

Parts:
R31: 18k; R_0805_HandSoldering
R32: 33K; R_0805_HandSoldering
U10: MPXV5050GP; mpxv5050gp_case1369_01
U11: BAV199; SOT-23

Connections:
+5V: U10.2 (VS_5V); also elsewhere on the board
/Filtrado/IN: R31.2, U10.4 (VOUT); also elsewhere on the board
/Sensor de presión/REG_OUT: R31.1, R32.1, U11.3 (C1/A2); also elsewhere on the board
GND: R32.2, U10.3 (GND), U11.1 (A1); also elsewhere on the board

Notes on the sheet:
SENSOR DE PRESIÓN
MPXV5050GP

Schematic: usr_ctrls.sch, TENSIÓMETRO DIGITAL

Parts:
C24, C25, C26: 100nF; C_0805_HandSoldering
D8: 1N4148; D_DO-35_SOD27_P10.16mm_Horizontal
R33, R34: 10k; R_0805_HandSoldering
R35: 4k7; R_0805_HandSoldering
SW3, SW4, SW5: SW_DPST; SW_Tactile_Straight_KSL0Axx1LFTR_edit

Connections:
/Controles de usuario/~SELECT: C24.1, R33.2, SW3.1, SW3.3; also elsewhere on the board
/Controles de usuario/~START: C25.1, R34.2, SW4.1, SW4.3; also elsewhere on the board
/microcontrolador/~MRESET: C26.1, D8.2 (A), R35.2, SW5.1, SW5.3; also elsewhere on the board
GND: C24.2, C25.2, C26.2, SW3.2, SW3.4, SW4.2, SW4.4, SW5.2, SW5.4; also elsewhere on the board

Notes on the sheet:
RESET MANUAL
START/STOP
SELECCIÓN / MENÚ
INTERFAZ DE USUARIO

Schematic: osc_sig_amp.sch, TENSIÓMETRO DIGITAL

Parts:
C3: 0.33uF; CP_Elec_4x5.7
C4: 33uF; CP_Elec_6.3x4.5
C5: 330uF; CP_Elec_8x10.5
R1: 24k; R_0805_HandSoldering
R6: 10k; R_0805_HandSoldering
R7: 1M; R_0805_HandSoldering
R8: 1k; R_0805_HandSoldering
R9: 120k; R_0805_HandSoldering
U1: LM358; VSSOP-8_2.3x2mm_Pitch0.5mm

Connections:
+5V: R1.1, U1.8 (V+); also elsewhere on the board
/Filtrado/IN: C3.1; also elsewhere on the board
/microcontrolador/FILTER: C5.1, R9.1, U1.1; also elsewhere on the board
GND: C4.2, C5.2, R6.2, U1.4 (V-), U1.5 (+), U1.6 (-); also elsewhere on the board
unnamed: C3.2, R7.2, U1.3 (+)
unnamed: C4.1, R8.2
unnamed: R1.2, R6.1, R7.1
unnamed: R8.1, R9.2, U1.2 (-)

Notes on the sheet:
Notas: - Como la salida del sensor MPVX5050GP y de este operacional son de 5v, y el ADC del LPC solo banca hasta 3v3 máx pongo un divisor resistivo. - En el encapsulado vienen dos operacionales. Las entradas que no se usan deben conecatse a GND para reducir el ruido.
FILTRADO
Amplificador de señal de oscilación

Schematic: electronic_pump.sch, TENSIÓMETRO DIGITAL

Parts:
D9: 1N4001; D_DO-41_SOD81_P10.16mm_Horizontal
J4: VALVE; TerminalBlock_bornier-2_P5.08mm
J5: AIR PUMP; TerminalBlock_bornier-2_P5.08mm
Q2, Q3: TIP31; TO-220-3_Vertical
R10: 330R; R_0805_HandSoldering
U2: 4N25; DIP-6_W7.62mm

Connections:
+5V: D9.1 (K), J5.2, Q2.2 (C); also elsewhere on the board
/Bomba de aire/BOMBA: R10.2; also elsewhere on the board
/Bomba de aire/VALVULA: Q2.1 (B); also elsewhere on the board
GND: J4.2, Q3.3 (E), U2.2; also elsewhere on the board
unnamed: D9.2 (A), U2.5
unnamed: J4.1, Q2.3 (E)
unnamed: J5.1, Q3.2 (C)
unnamed: Q3.1 (B), U2.4
unnamed: R10.1, U2.1

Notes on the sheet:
VÁLVULA Y BOMBA DE AIRE

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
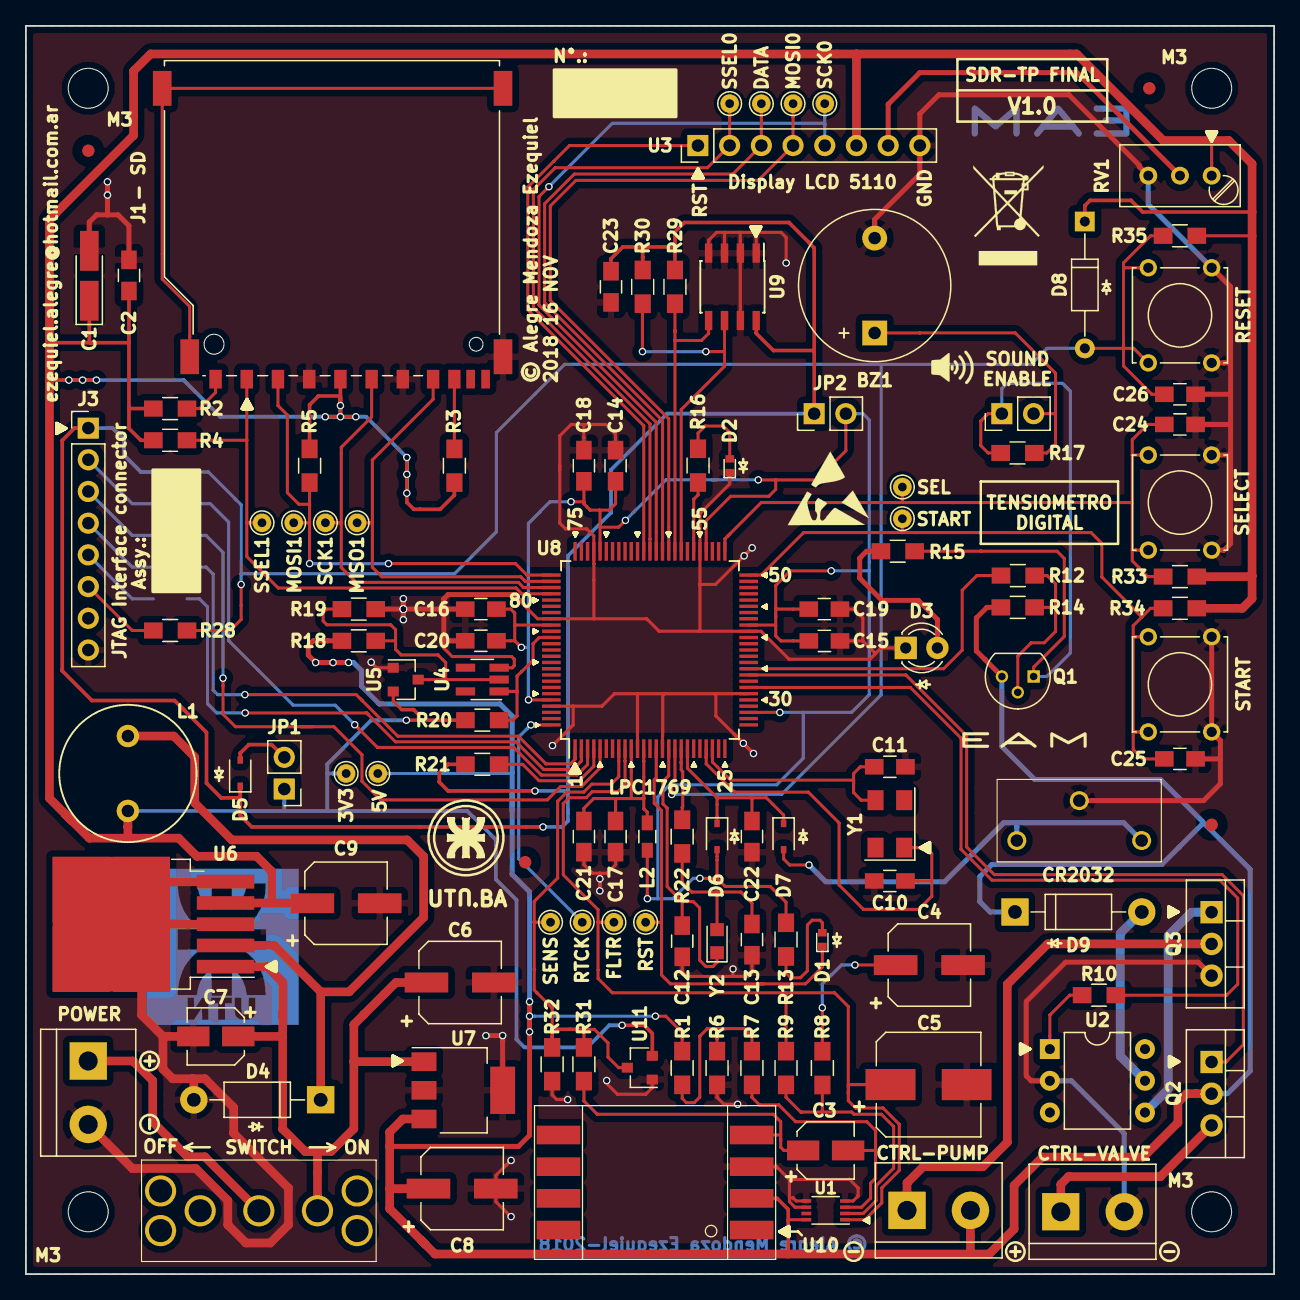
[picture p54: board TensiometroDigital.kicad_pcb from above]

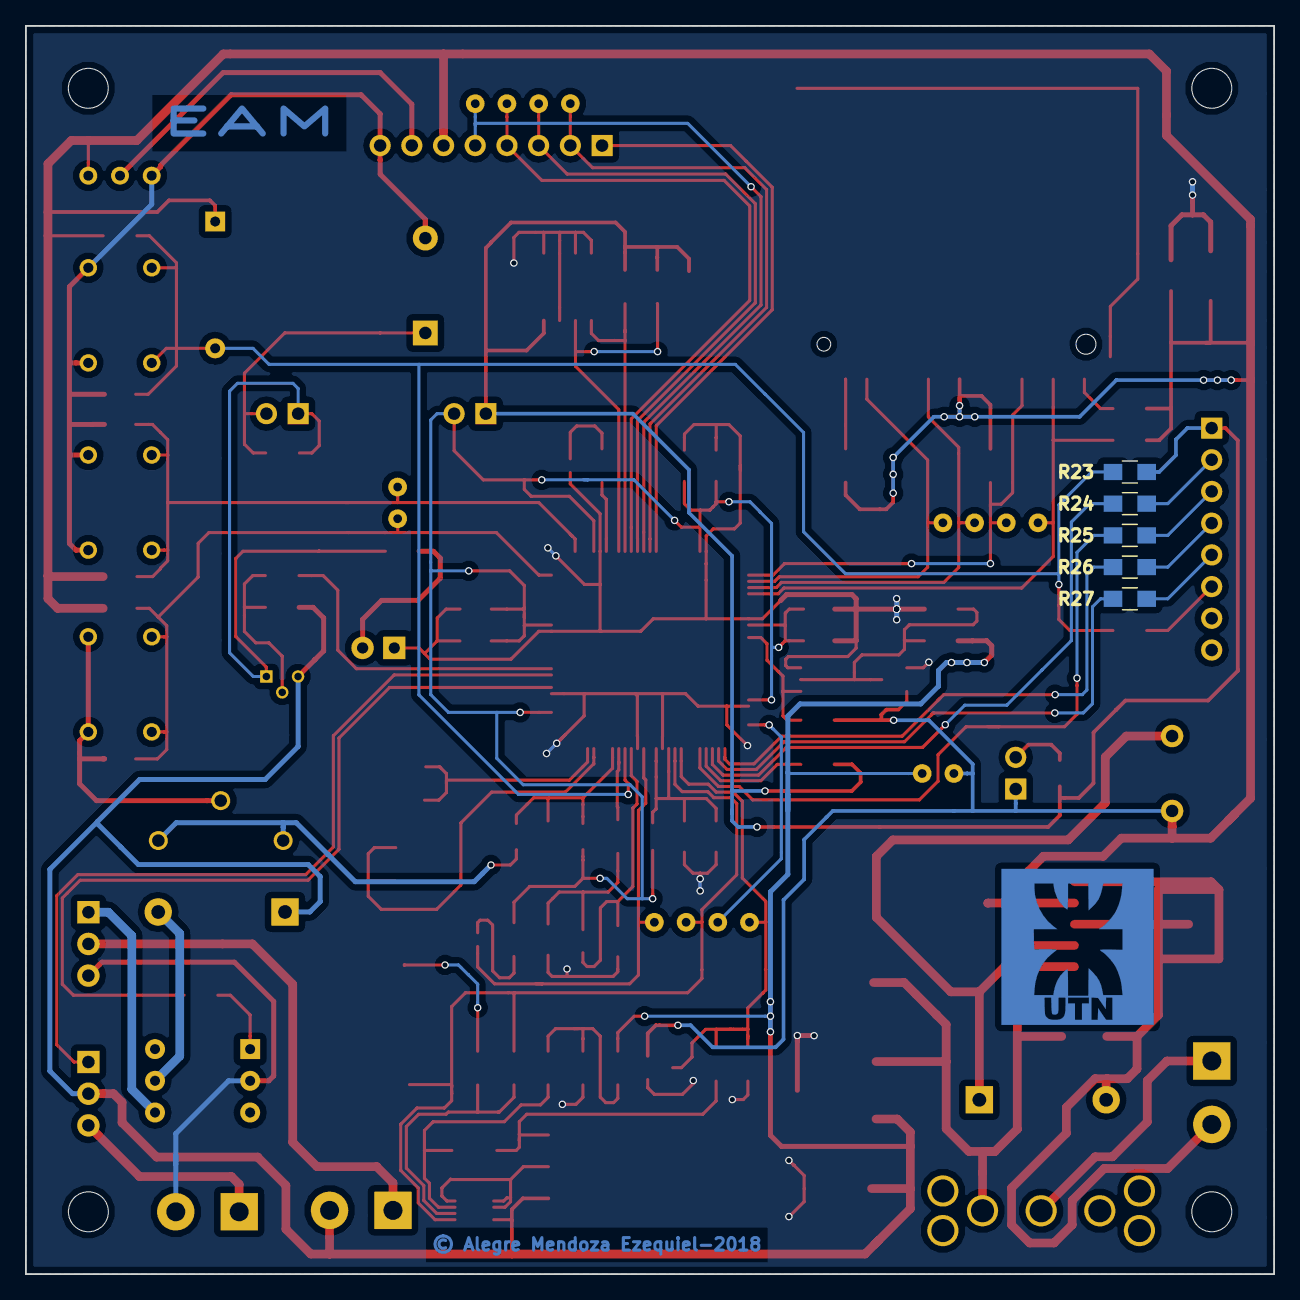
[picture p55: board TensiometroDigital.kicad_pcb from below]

Board: 2 copper layers, 100.0 x 100.0 mm, 126 parts (5 on the bottom side), 70 nets.

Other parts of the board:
F: Fiducial_1mm_Dia_2.54mm_Outer_CopperTop
F#2, F#3, F#4: Fiducial_1mm_Dia_2.54mm_Outer_CopperTop
M3, M3#2, M3#3, M3#4: MountingHole_3.2mm_M3

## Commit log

2018-09-03 pcb update
    [TensiometroDigital.kicad_pcb, TensiometroDigital.sch]
2018-09-03 pcb update 2
2018-10-18 cambios al sch
    [TarjetaSD.sch, TensiometroDigital.sch, buzzerNled.sch, display_Nokia5110.sch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]
2018-11-20 Finalizado: SCH, PCB, GABINETE, DRAWINGS. FALTA: GERBERS, BOM e Informe
    [41812.stp, 70746593.stp, Coilcraft-RFC1010B.STEP, PCB Layout Checklist.xlsx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]
2018-11-20 Agregados GERBERS. Falta BOM e Informe
    [TensiometroDigital-B.Cu.gbr, TensiometroDigital-B.Mask.gbr, TensiometroDigital-B.Paste.gbr, TensiometroDigital-B.SilkS.gbr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]
2018-11-20 Creada la BOM
    [TensiometroDigital.xlsx, mc34064.sch]
2018-11-23 TP FINALIZADO. FALTA CREAR EL ZIP
    [TensiometroDigital.kicad_pcb, pcb.fcstd]
2018-11-23 TP FINALIZADO. ZIP PARA ENTREGAR
    [TensiometroDigital-B.Cu.gbr, TensiometroDigital-B.Mask.gbr, TensiometroDigital-B.Paste.gbr, TensiometroDigital-B.SilkS.gbr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]

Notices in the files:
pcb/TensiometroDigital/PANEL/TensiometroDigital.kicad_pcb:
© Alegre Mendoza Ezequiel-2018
